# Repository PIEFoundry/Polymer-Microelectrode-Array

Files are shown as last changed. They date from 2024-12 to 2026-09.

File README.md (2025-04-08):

# Polymer Microelectrode Array
This repository contains all files relevant to the design and manufacture of the PIE Foundry polymer microelectrode arrays. For more information about the PIE Foundry, visit our [website](https://piefoundry.usc.edu/). <br>
Please cite this repository using the DOI below <br> 

## Organization
[Protocols](/Protocols) directory holds up-to-date protocols and subprotocols for PMEA microfabrication and PCB attachment/packaging. PDF files are updated with each release. <br>
[Designs](/Designs) directory holds lithographic designs of open-source PMEAs produced by the PIE Foundry, including component designs for lithographic masks, and PCB designs of common adapter boards. Lithographic designs are stored as .dxf and PCB designs are stored as gerber files and Eagle schematics. <Br>
[Resource](/Resources/) directory holds PIE Foundry generated Eagle libraries, including for common PMEA wirebond connector layouts and Omnetics brand analog connector solder pad layouts, as well as useful solid files. Solid files are stored in STEP format. 

## License
All files in this repository are released under the CC-BY 4.0 International copyright license

## Disclaimer
The contents of this repository are subject to revision. No representation or warranty, express or implied, is provided in relation to the accuracy, correctness, completeness, or reliability of the information, opinions, or conclusions expressed in this repository.

The contents of this repository (the “Materials”) are experimental in nature and should be used with prudence and appropriate caution. Any use is voluntary and at your own risk.

The Materials are made available “as is” by USC (the University of Southern California and its trustees, directors, officers, employees, faculty, students, agents, affiliated organizations and their insurance carriers, if any), and any other contributors to this repository (collectively, “Providers”). Providers expressly disclaim all warranties, express or implied, arising in connection with the Materials, or arising out of a course of performance, dealing, or trade usage, including, without limitation, any warranties of title, noninfringement, merchantability, or fitness for a particular purpose.

Any user of the Materials agrees to forever indemnify, defend, and hold harmless Providers from and against, and to waive any and all claims against Providers for any and all claims, suits, demands, liability, loss or damage whatsoever, including attorneys' fees, whether direct or consequential, on account of any loss, injury, death or damage to any person or (including without limitation all agents and employees of Providers and all property owned by, leased to or used by either Providers) or on account of any loss or damages to business or reputations or privacy of any persons, arising in whole or in part in any way from use of the Materials or in any way connected therewith or in any way related thereto.

The Materials, any related materials, and all intellectual property therein, are owned by Providers.

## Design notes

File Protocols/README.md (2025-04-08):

These are the current microfabrication, packaging, and assembly protocols for manufacturing Parylene C based microelectrode arrays. Protocols were developed by PIE Foundry staff and derived from work at the [Biomedical Microsystems Laboratory](http://biomems.usc.edu/) of Dr. Ellis Meng at the University of Southern California. 

Contributors: Kee Scholten, Jessica Ortigoza-Diaz, James Yoo, Artin Petrossians, Rachael Gallonio, Steven Baldwin, Ellis Meng

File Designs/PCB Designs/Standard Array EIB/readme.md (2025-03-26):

PCB design file set for 64 channel Standard Array EIB

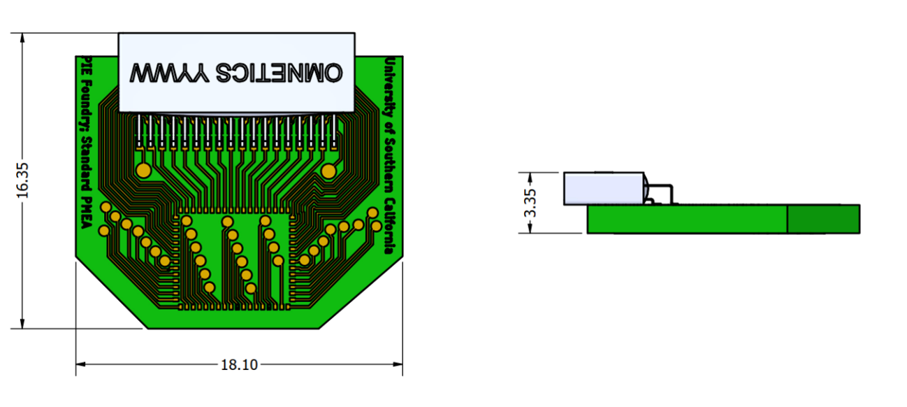
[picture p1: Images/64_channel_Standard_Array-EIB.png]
Image of a printed circuit board schematic


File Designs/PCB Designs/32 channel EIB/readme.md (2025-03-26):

PCB design file set for 32 channel EIB 

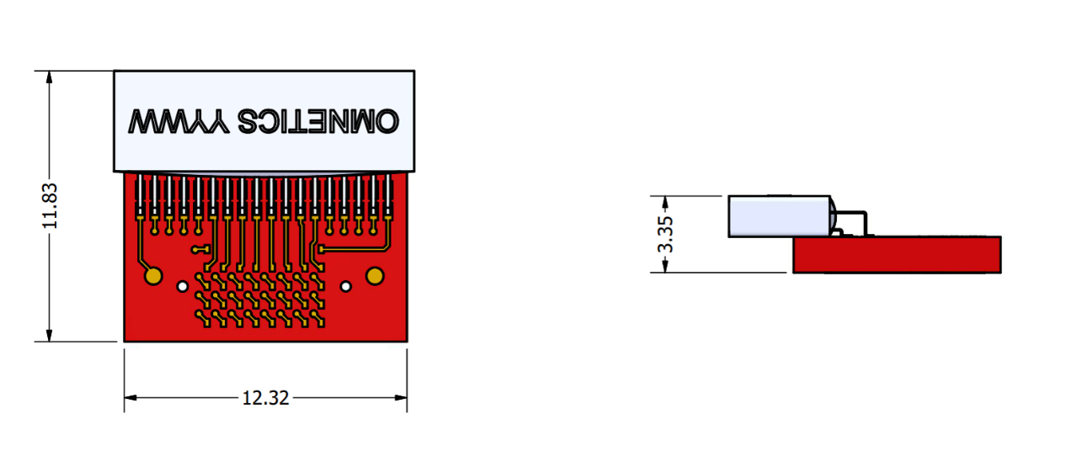
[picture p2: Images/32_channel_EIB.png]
Image of a printed circuit board schematic


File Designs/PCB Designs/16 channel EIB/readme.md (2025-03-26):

PCB design file set for 16 channel EIB 

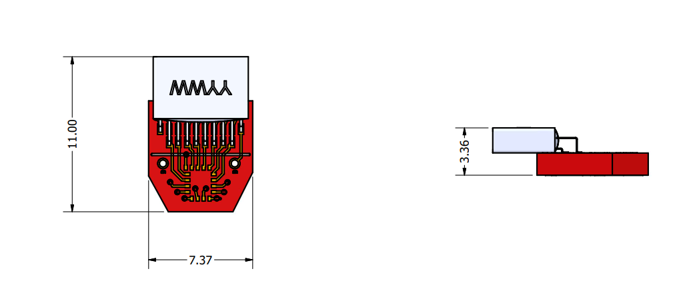
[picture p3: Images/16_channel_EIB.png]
Image of a printed circuit board schematic


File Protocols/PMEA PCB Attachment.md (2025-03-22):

# Protocol: Packaging and Assembly of Parylene Microelectrode Arrays

Description: This document details the packaging and assembly protocol for connectorization of Parylene C microelectrode arrays (MEAs) with printed circuit board (PCB) connectors.

_Note: Standard equipment and materials (e.g. tweezers, microscopes, DI water, cleanroom wipes, N<sub>2</sub> gun, scale, etc.) are not listed in materials lists._

Table of Contents

1. [Printed Circuit Board (PCB) Preparation](#1-pcb-preparation)
   * [Separate, Sand, and Clean](#11-separate-sand-and-clean)
   * [Bump Contact Pads](#12-bump-contact-pads)
   * [Coin Contact Pads](#13-coin-contact-pads)
2. [Component/Connector Soldering](#2-componentconnector-soldering)
      * [Apply Solder Paste](#21-apply-solder-paste)
      * [Align and Attach Components](#22-align-and-attach-components)
      * [Reflow Solder](#23-reflow-solder)
      * [Clean PCB](#24-clean-pcb)
3. [Parylene C Coating](#3-parylene-c-coating)
      * [Mask Components](#31-mask-components)
      * [Deposit Parylene C](#32-deposit-parylene-c)
4. [Component Potting & Ground Attachment](#4-component-potting--ground-attachment)
      * [Pot Connectors](#41-pot-connectors)
      * [Demask](#42-demask)
      * [Solder Ground Wires](#43-solder-ground-wires)
5. [Polymer Ultrasonic on Bump (PUB) Bonding](#5-polymer-ultrasonic-on-bump-pub-bonding)
      * [Align MEA to PCB](#51-align-mea-to-pcb)
      * [PUB Bond MEA to PCB](#52-pub-bond-mea-to-pcb)
6. [Underfill & Overcoat](#6-underfill--overcoat)
      * [Underfill](#61-underfill)
      * [Overcoat](#62-overcoat)
<ol type="A">
  <li>     <a href="#a-material-sources">Material Source</a>   </li>
  <li>     <a href="#b-equipment-models">Equipment Models</a>   </li>
</ol>

## 1. PCB Preparation

### 1.1 Separate, Sand, and Clean
_Note: This section only applies to FR-4 PCBs_

Materials: 
* *400 grit sandpaper (or similar)*
* *Isopropanol*

Equipment: 
* *Ultrasonic cleaner*

Process:
1. Separate PCBs from panel.
2. Sand edges with 400 grit sandpaper.
   1. With sandpaper flat on desk or table, run PCB edges across sandpaper until smooth. Apply even force to keep edges flat.
3. Clean PCBs in ultrasonic cleaner.
   1. Isopropanol for 10 minutes
   2. DI water for 10 minutes
4. Blow dry with N<sub>2</sub>

### 1.2 Bump Contact Pads

Equipment: 
* *Ultrasonic wire bonder (ball type)*

Process:
1. Using a ball-bonder in bump mode, place two gold bumps, approximately 75 microns in diameter, on the center of each contact pad on the PCB.
    1. Bump parameters
   <br>Tool: Hybond Model 626
   <br>Gold wire: 1 mil
   <br>Capillary attachment: Small Precision Tools UTSDIC-38HH-AZM-1/16-19MM
   <br>Stage Temperature: 140 °C
   <br>Ultrasonic Power: 180 mW
   <br>Time: 180 miliseconds
   <br>Force: 12 grams
   <br>EFO Power: 29 arbitrary units
   <br>Pull Length: 02 units
   <br>Tail Length: 27 units
    <br>Loop Height: 010 units

2. For best results ensure PCB is flush with stage and held tightly by clamps and/or vacuum chuck. For flex-PCBs additional fixturing may be required. Above parameters are tailored for FR-4 and may need to be modified for flex-PCB.

### 1.3 Coin Contact Pads

Equipment: 
* *Ultrasonic wire bonder (ball or wedge type)*

Process:
1. Using an ultrasonic ball bonder or wedge bonder with a tape-automated-bonding (TAB) tool attachment flatten and level each gold bump into a ‘coin’. Each bump will be hit twice with the two separate settings below.
    1. Tool: Hybond Model 572a
   <br>Tab attachment: Small Precision Tools 7045W-C-9060-3/4-M
   <br>Stage Temperature: Room temperature  
   <br>Step #1:  
   <br>Ultrasonic Power: 3 units
   <br>Time: 4.4 units
   <br>Force: 5.0 units  
   <br>Step #2:  
   <br>Ultrasonic Power: 3.4 units
   <br>Time: 4.4 units
   <br>Force: 7.0 units

2. Resulting coins should be approximately 30 microns tall and 100 microns in diameter.

## 2. Component/Connector Soldering

### 2.1 Apply Solder Paste

Materials: 
* *Lead-free solder paste*
* *23-gauge Luer stub (4 mm in length)*

Equipment: 
* *Pneumatic fluid dispenser*
* *Stereoscope*

Process:
1. Remove solder-paste from refrigerator and allow to reach room temperature, approximately 20 minutes.
2. Connect solder-paste cartridge to fluid dispenser.
    1. Attach Luer stub
    2. Set dispenser to 15 PSI
3. With aid of stereoscope, apply a small dot of solder past to each solder pad. Paste should be dispensed in one motion for each pad.

### 2.2 Align and Attach Components

Equipment: 
* *Soldering iron*
* *Stereoscope*

Process:
1. With aid of stereoscope carefully place and align components onto solder pads.
    1. For components such as Omnetics connectors which often hang off the edge of the PCB, a spacer may be necessary.
2. With the soldering iron set to~650 °F solder a single outside leg of each component.
    1. If necessary, adjust alignment and solder a leg on the other side of the component.

### 2.3 Reflow Solder

Materials: 
* *Ceramic plate or stainless-steel tray*

Equipment:
* *Reflow oven*

Process:
1. Place PCBs to be soldered in stainless-steel tray or onto ceramic plate and place on reflow oven platform.
2. Solder components to PCB using reflow oven with following profile:
    1. Tool: DDM Novastar Model GF-B
   <br>Temperature: 240 °C
   <br>Time<sub>a</sub>: 90 seconds
   <br>Time<sub>b</sub>: 300 seconds

### 2.4 Clean PCB

Materials: 
* *Lead-free flux remover*
* *Isopropanol*

Equipment: 
* *Ultrasonic cleaner*

Process:
1. Descum (clean) wafers in the RIE, two 4” wafers at the same time, using the following recipe:  
    150 mT, 100 W, 50 sccm O<sub>2</sub>, 180 s.

## 3. Parylene C Coating

### 3.1 Mask Components

Materials:
* *PTFE tape*

Process:
1. Using thin PTFE tape, cover the bond pads, faces of all connectors, solder connectors for ground/reference wire attachment, and any other surface needed to be deinsulated
    1. PCB designs with vias may need to be masked on both sides to prevent Parylene C from diffusing through vias underneath masking tape.
    2. Tape must be snug; use tweezer, dental pick, or other small metal tool to firmly laminate tape over all surfaces.

### 3.2 Deposit Parylene C

Materials:
* *Parylene C dimer*

Equipment:
* *Parylene PVD*

Process:
1. Deposit 10 µm of Parylene C onto the PCBs. See Parylene C Deposition Protocol.
    1. 30 g of dimer is typical but will depend on number and size of PCBs.
    2. As Parylene C layer on PCBs cannot be measured directly, reference slides should be included in coating.
    3. PCBs should be placed on sheet of aluminum foil in coating system to prevent them from sticking to shelves.

## 4. Component Potting & Ground Attachment

### 4.1 Pot Connectors

Materials: 
* *Medical grade epoxy*
* *23-gauge Luer stub*
* *3 cc dispenser barrel*
* *Dispenser cap*

Equipment: 
* *Pneumatic fluid-dispenser*
* *Bell jar*
* *Scale*
* *Oven*

Process:
1. Weigh out and thoroughly mix components of medical grade epoxy.
    1. For Epotek MED-302-3M (preferred) the ratio is 10:4.5.
    2. 1-2 g is sufficient
2. Decant epoxy into dispenser barrel and degas in bell jar under vacuum for 1 hour
    1. Barrel should be capped and stood vertically to prevent epoxy from spilling or leaking
3. Connect barrel to fluid dispenser.
    1. Attach Luer stub
    2. Set dispenser to 15 PSI
4. Apply a thick layer of epoxy to all exposed component legs.
5. Cure in oven according to epoxy curing schedule
    1. For MED-302-3M this is 2 hours at 80 °C

### 4.2 Demask

Materials:
* *Isopropanol*
* *Razor or X-Acto knife*

Equipment: 
* *Ultrasonic bath*
* *Stereoscope*

Process:
1. Using a fresh razor blade or X-Acto knife remove the Parylene C insulation from the masking tape.
2. Soak the masking tape with isopropanol and gently remove the tape from contact pads and solder connections.
3. Clean PCBs in ultrasonic cleaner.
    1. Isopropanol for 5 minutes
    2. DI water for 5 minutes
    3. Blow dry with N<sub>2</sub>

### 4.3 Solder Ground Wires

Materials:
* *Fine, insulated, stainless-steel wires (0.003” bare, 0.0055” coated, annealed)*
* *Lead-free solder*
* *Stainless steel flux*
* *Micro swab*
  
Equipment: 
* *Soldering iron*
* *Stereoscope*
* *Micro scissors*

Process:
1. Cut 8-10 cm lengths of stainless-steel wire (typically 2 per PCB) and remove 1 cm of insulation from proximal end, and 3 cm from the distal end.
    1. Use stainless steel micro scissors to carefully strip insulation.
    2. Length and number of ground wire may vary with project design
2. Thread proximal end of wire through appropriate plated-through-hole on PCB. Bend de-insulated end to prevent wire from pulling out.
3. Using micro swab, apply small dab of stainless-steel flux to soldering site.
4. With soldering iron set to 650 °F, solder wire to board using lead-free solder.
5. Trim excess wire from underside of PCB.
6. Repeat as needed for each wire.

## 5. Polymer Ultrasonic on Bump (PUB) Bonding

### 5.1 Align MEA to PCB

Materials:
* *Adhesive tape*
  
Equipment: 
* *Stereoscope*

Process:
1. Place MEA face down over PCB contact pads.
2. Using stereoscope, align MEA to contact pads and secure in place with small pieces of tape.
    1. It is very important that the Parylene C MEA lies as flat as possible. If necessary small drops of isopropanol can be used to pull the MEA taught to the PCB using surface tension.

### 5.2 PUB Bond MEA to PCB

Equipment:
* *Ultrasonic wire bonder (ball or wedge type)*

Process:
1. Using an ultrasonic wire bonder with a tape-automated bonding (TAB) tool attachment, weld each contact pad on the Parylene MEA to the corresponding PCB pad, using the flattened gold coins as an intermediary. Each pad will be hit twice with the two separate settings below.
    1. Tool: Hybond Model 572A
   <br> Tab attachment: Small Precision Tools 7045W-TI-10050-3/4-M
   <br> Stage Temperature: Room temperature
   <br> Step #1:
   <br> Ultrasonic Power: 8.0 units
   <br> Time: 3.0 units
   <br> Force: 6.5 units
   <br>Step #2:
   <br> Ultrasonic Power: 9.0 units
   <br> Time: 4.5 units
   <br> Force: 6.0 units

    2.  Take all measures to try and keep the MEA laminated to the PCB

## 6 Underfill & Overcoat

### 6.1 Underfill

Materials: 
* *Medical grade epoxy (thin)*
* *32-gauge Luer stub*
* *3 cc dispenser barrel*

Equipment: 
* *Pneumatic fluid-dispenser*
* *Scale*
* *Stereoscope*
* *Oven*

Process:
1. Weigh out and thoroughly mix components of medical grade epoxy.
    1. For Epotek MED-301 (preferred) the ratio is 20:5
    2. 1 g is sufficient
2. Fill cartridge with epoxy and connect barrel to fluid dispenser.
    1. Attach Luer stub
    2. Set dispenser to 10 PSI
3. Apply small drops of epoxy to the edges/corners of the MEA and allow to underfill the space between the MEA and the PCB.
4. Allow to cure at room temperature (overnight) or in oven at 65 °C for 1 hour.

### 6.2 Overcoat

Materials: 
* *Medical grade epoxy*
* *23-gauge Luer stub*
* *3 cc dispenser barrel*
* *Dispenser cap*

Equipment: 
* *Pneumatic fluid-dispenser*
* *Bell jar*
* *Scale*
* *Oven*

Process:
1. Weigh out and thoroughly mix components of medical grade epoxy.
    1. For Epotek MED-302-3M (preferred) the ratio is 10:4.5
    2. 1-2 g is sufficient
2. Decant epoxy into dispenser barrel and degas in bell jar under vacuum for 1 hour
    1. Barrel should be capped and stood vertically to prevent epoxy from spilling or leaking
3. Connect barrel to fluid dispenser.
    1. Attach Luer stub
    2. Set dispenser to 15 PSI
4. Apply a thick layer of epoxy to entire surface of PCB
5. Cure in oven according to epoxy curing schedule
    1. For MED-302-3M this is 2 hours at 80 °C
6. Repeat on opposite side
7. Material Sources

_Note: Standard materials (e.g. isopropanol, DI water, cleanroom wipes, etc.) are not listed_

## A. Material Sources
| **Material** | **Model #** | **Supplier** |
| --- | --- | --- |
| Parylene C dimer |     | Specialty Coating Systems, Indianapolis, IN |
| Lead-free solder paste | 4900 P SAC305 | MG Chemicals, Burlington, Ontario, Canada |
| Lead-free flux remover | ES1697 | Chemtronics, Kennesaw, Georgia |
| Medical grade epoxy (thick) | MED-302-3M | Epoxy Technology, Billerica, MA |
| Medical grade epoxy (thin) | MED-301 | Epoxy Technology, Billerica, MA |
| Stainless-steel flux |     | Superior Flux & Mfg. Co., Cleveland, OH |
| Stainless-steel wire | 790900 | A-M Systems Inc., Sequim, WA |
| Dispenser barrel |     | North Richland Hills, TX |

## B. Equipment Models

_Note: Standard equipment (e.g. tweezers, microscopes, N<sub>2</sub> gun, scale, etc.) are not listed_

| **Equipment** | **Model #** | **Supplier** |
| --- | --- | --- |
| Ultrasonic wire bonder (ball type) | 626 | Hybond Inc., Escondido, CA |
| Ultrasonic wire bonder (wedge type) | 572A | Hybond Inc., Escondido, CA |
| Ball-bonder capillary | UTSDIC-38HH-AZM-1/16-19MM | Small Precision Tools, Petaluma, CA |
| TAB tool | 7045W-C-9060-3/4-M | Small Precision Tools, Petaluma, CA |
| 7045W-TI-10050-3/4-M |
| Pneumatic fluid-dispenser | Performus III | Nordson, Westlake, OH |
| Reflow oven | GF-B | DDM Novastar, Ivyland, PA |
| Parylene PVD | PDS 2010 Labcoter | Specialty Coating Systems, Indianapolis, IN |

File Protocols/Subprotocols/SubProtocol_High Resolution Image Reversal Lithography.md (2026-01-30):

# Sub-Protocol: High Resolution Image Reversal Lithography

Description: This document details the protocol for the high-resolution image reversal lithography used to produce the lift-off profile for metal patterning in the PIE Foundry standard microfabrication process. It is tailored for use on Parylene C coated silicon wafers.

## Materials:

* *AZ5214-E Photoresist*
* *AZ340 Developer*
* *5 mL Polypropylene Syringe (per wafer)*
* *22-Gauge Luer Stub (per wafer)*

## Equipment:

* *OAI Model 200 Contact Mask Aligner and UV Source*
* *Electronic Micro Systems 1000-1 Hot plate*
* *YES CV200RFS Plasma Asher*
* *Laurell Technologies Photoresist Spinner Model WS-400B-6NPP Lite*
* *Vacuum oven with N<sub>2</sub>*
* *UV intensity meter*
* *IR temperature sensor*
* *Wafer centering tool*
* *HDPE trays for developer and water baths*
* *Wafer dipper/holding tool*

## Parameters:

### Spinner Recipe Program P  
1st Spin Speed: 500 RPM  
1st Spin Time: 10 seconds<br>
1st Spin Acceleration: acceleration level 8 (1088 RPM)  
<br>
2nd Spin Speed: 4200 RPM  
2nd Spin Time: 40 seconds<br>
2nd Spin Acceleration: acceleration level 8 (1088 RPM)

### Soft-Bake
Temperature: 110 °C
Time: 60 seconds

### 1st Exposure
Dose: 42 mJ/cm<sup>2</sup>
Time: 3.4 seconds
Intensity: 12.5 mW/cm<sup>2</sup>

### Image-Reversal Bake
Temperature: 110 °C
Time: 63 seconds

### 2nd Exposure
Dose: 280 mJ/cm<sup>2</sup><br>
Time: 22.4 seconds<br>
Intensity: 12.5 mW/cm<sup>2</sup>

### Develop
Concentration: 1:4 AZ340 developer to deionized water (200 mL total volume)<br>
Time: 18 seconds

## Process:

1.  Descum
    1. Descum (clean/roughen) wafers in the asher using the following recipe<br>
   300 mT, 100 W, 115 sccm O<sub>2</sub>, 300 seconds

2. Prepare Developer and Water Baths<br>
_Note: perform in chemical fume hood_
    1. Prepare a shallow HDPE tray full of DI water, and with a 1:4 mixture of AZ340 developer and DI water (200 mL total volume)
    <br> a. 200 mL of developer solution should be sufficient for 2 wafers

3. Dry-Bake<br>
_Note: this step should be performed immediately before photoresist deposition_
    1. Bake wafers at 60 °C in an oven under light vacuum (35-40 cmHg) and N<sub>2</sub> flow (15-20 sccm) for >15 minutes

4. Spin Photoresist<br>
_Note: Before coating wafers run 3 “dummy spins” using spare wafers to ensure spinner chamber environment is saturated with solvent from photoresist. This will prevent differences in resist thickness between first and last wafers in a run._
    1. Line sidewalls of spinner with aluminum foil to reduce mess
    2. Center wafer on spinner vacuum chuck using spinner centering tool and engage chuck vacuum
    <br> a. Spinner requires supply of clean dry air for vacuum to engage
    3. Deposit 3 mL of AZ5214-E photoresist from preprepared syringe onto center of wafer through 22-gauge Luer stub
    <br> a. Ensure there are no air bubbles in resist
    4. Close lid and run program
    <br> a. Spin on 500 RPM for 10 seconds
    <br> b. Spin 4200 RPM for 40 seconds

5. Soft-Bake
    1.Bake the wafer on hotplate for 1 minute at 110 °C. Calibrate temperature to IR gun and do not rely on hotplate reading
    2. Wafer should be placed in the center of the hot plate with flat facing forward. Use heat shield around hot plate
    3. After baking, store the wafer in black wafer storage box for at least 3 minutes

6. Vacuum Contact and Exposure
    1. Set the UV lamp to desired intensity and duration. Targeted dose is 42 mJ/cm<sup>2</sup>. Typical intensity is 12.5 mW/cm<sup>2</sup> for 3.4 seconds but can be adjusted depending on current lamp intensity
    2. Clean mask aligner vacuum chuck and mask holder of any particles. Place vacuum O-ring around vacuum chuck
    3. Place photomask feature (chrome) side down (facing vacuum chuck). Secure with mask holder vacuum and screw clamps
    4. Place wafer face up and centered on vacuum chuck. Turn on substrate vacuum
    5. Blow mask surface and wafer surface clean of particles with N<sub>2</sub> gun
    6. Engage N<sub>2</sub> purge
    7. Lower mask holder
    8. Raise wafer using Z-axis knob until mask appears flush with mask. Lower mask slightly and then use fine x/y/θ controls to center wafer under mask. Re-raise wafer
    9. Turn off substrate vacuum and engage contact vacuum. Open contact vacuum knob until vacuum gauge reads ~5” Hg. You may need to lower N<sub>2</sub> purge to create good seal. Please note, sufficient vacuum is only needed to create good contact between mask and wafer as indicated by appearance of Newton ring diffraction. Use the lowest possible vacuum setting that will achieve this effect
    10. Expose the wafer by carefully sliding the aligner assembly under the UV lamp. Wait for exposure, then carefully slide the assembly back to starting position
    11. Lower the contact vacuum level by turning the knob clockwise. Once closed, turn off the contact vacuum. If the N<sub>2</sub> purge level was decreased, return it to starting level. Re-engage the substrate vacuum and then gently lower the wafer. If the wafer does not move freely, pause, and wait before trying again
    12. Lower the wafer completely clear of the mask. Raise the mask holder. Dis-engage substrate vacuum and N<sub>2</sub> purge. Remove wafer

7. Image-Reversal-Bake
    1. Bake the wafer on hotplate for 63 seconds at 110 °C ± 0.5 °C. Calibrate temperature to IR gun and do not rely on hotplate reading
    <br> a. This step is critical. Avoid any variation in time or temperature
    2. Wafer should be placed in the center of the hot plate with flat facing forward. Use heat shield around hot plate
    3. After baking, store the wafer in black wafer storage box for at least 3 minutes

8. Flood Exposure
    1. Set the UV lamp to desired intensity and duration. Targeted dose is 280 mJ/cm<sup>2</sup>. Typical intensity is 12.5 mW/cm<sup>2</sup> for 22.4 seconds but can be adjusted depending on current lamp intensity
    2. Remove mask from mask holder and store
    3. Place wafer face up and centered on vacuum chuck. Turn on substrate vacuum
    4. Blow wafer surface clean of particles with N<sub>2</sub> gun
    5. Expose the wafer by carefully sliding the aligner assembly under the UV lamp. Wait for exposure, then carefully slide the assembly back to starting position
    6. Dis-engage substrate vacuum. Remove wafer

9. Quench in Deionized Water
    1. Immediately place wafer in shallow bath of DI water and let soak for 3 minutes to avoid heating and reduce gas bubble formation

10. Develop
    1. Develop wafer in 1:4 solution of AZ340 to DI water for 18 seconds with mild agitation
    2. Immediately rinse in DI water bath and rinse 3× in water
    3. Blow dry with N<sub>2</sub>

11. Inspect
    1. Inspect under compound microscope with yellow light filter

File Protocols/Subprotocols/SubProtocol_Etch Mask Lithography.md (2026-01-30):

# Sub-Protocol: Etch Mask Lithography

Description: This document details the protocol for the photolithography used to produce the etch mask used to define the pattern in (deep) reactive ion etching steps in the PIE Foundry MEA microfabrication process. This protocol is tailored for use on Parylene C coated silicon wafers.

## Materials:

* *AZ 12XT-20PL-15 Photoresist*
* *726 MIF Developer*
* *5 mL Polypropylene Syringe (per wafer)*

## Equipment:

* *OAI Model 200 Contact Mask Aligner and UV Source*
* *Electronic Micro Systems 1000-1 Hot plate*
* *YES CV200RFS Plasma Asher*
* *Laurell Technologies Photoresist Spinner Model WS-400B-6NPP Lite*
* *Vacuum oven with N<sub>2</sub>*
* *UV intensity meter*
* *IR temperature sensor*
* *Wafer centering tool*
* *HDPE trays for developer and water baths*
* *Wafer dipper/holding tool*

## Parameters

Spinner Recipe Program T  
1st Spin Speed: 500 RPM  
1st Spin Time: 10 seconds

1st Spin Acceleration: acceleration level 2 (low acceleration/deceleration)  
2nd Spin Speed: 2000 RPM  
2nd Spin Time: 45 seconds

2nd Spin Acceleration: acceleration level 2 (low acceleration/deceleration)

### Soft-Bake:<br>
Temperature: 110 °C<br>Time: 180 seconds 

### Exposure<br>
Dose: 117.5 mJ/cm<sup>2</sup><br>
Time: 9.4 seconds<br>
Intensity: 12.5 mW/cm<sup>2</sup>

### Post-Exposure Bake

Temperature: 90 °C<br>
Time: 90 seconds

### Develop

Concentration: 726 MIF developer as bottled<br>
Time: 75 seconds (approximate)

## Process:

1. Descum
    1. Descum (clean/roughen) wafers in the asher using the following recipe  :
    2. 300 mT, 100 W, 115 sccm O<sub>2</sub>, 300 seconds
2. Prepare Developer and Water Baths<br>_Note: perform in chemical fume hood_
    1. Prepare a shallow HDPE tray full of DI water, and another with 726 MIF developer
    <br> a. ~250 mL of 726 MIF developer should be sufficient for 6 wafers

3. Dry-Bake<br>_Note: this step should be performed immediately before photoresist deposition_
    1. Bake wafers at 60 °C in an oven under light vacuum (35-40 cmHg) and N¬2 flow (15-20 sccm) for >15 minutes

4. Spin Photoresist<br>_Note: Before coating wafers run 3 “dummy spins” using spare wafers to ensure spinner chamber environment is saturated with solvent from photoresist. This will prevent differences in resist thickness between first and last wafers in a run._
    1. Line sidewalls of spinner with aluminum foil to reduce mess
    2. Center wafer on spinner vacuum chuck using spinner centering tool and engage chuck vacuum
    <br> a. Spinner requires supply of clean dry air for vacuum to engage
    3. Deposit 3 mL of AZ 12XT-20PL-15 photoresist from preprepared syringe onto center of wafer
    <br> a. Ensure there are no air bubbles in resist
    4. Close lid and run program
    <br> a. Spin on 500 RPM for 10 seconds
    <br> b. Spin 2000 RPM for 45 seconds <br>_Note: Low acceleration/deceleration helps prevent spin defects_

5. Edge Bead Removal
    1. Remove photoresist edge bead to improve lithographic alignment. [See Edge Bead Removal Subprotocol](SubProtocol_Edge%20Bead%20Removal.md) 

6. Soft-Bake
    1. Bake the wafer on hotplate for 3 minutes at 110 °C. Calibrate temperature to IR gun and do not rely on hotplate reading
    2. Wafer should be placed in the center of the hot plate with flat facing forward. Use heat shield around hot plate
    3. After baking, store the wafer in black wafer storage box for at least 3 minutes

7. Align, Contact, and Exposure
    1. Set the UV lamp to desired intensity and duration. Targeted dose is 117.5 mJ/cm<sup>2</sup>. Typical intensity is 12.5 mW/cm<sup>2</sup> for 14.8 seconds but can be adjusted depending on current lamp intensity
    2. Clean mask aligner vacuum chuck and mask holder of any particles. Remove vacuum O-ring around vacuum chuck if present
    3. Place photomask feature (chrome) side down (facing vacuum chuck). Secure with mask holder vacuum and screw clamps
    4. Place wafer face up and centered on vacuum chuck. Turn on substrate vacuum
    5. Blow mask surface and wafer surface clean of particles with N<sub>2</sub> gun
    6. Engage N<sub>2</sub> purge
    7. Lower mask holder
    8. Raise wafer using Z-axis knob until mask is flush with mask. Engage ball lock
    9. Reduce Z-axis control sensitivity. While looking through aligner microscope on lowest magnification, lower wafer until it just barely disengages with mask. Confirm that wafer is now able to move freely using fine X/Y/θ controls
    10. Moving back and forth between left and right alignment marks, align the angle (theta) of the mask and wafer
    11. Once wafer and mask are aligned in theta, ensure X and Y coordinates are aligned
    12. Increase magnification to higher objective lens then repeat 5.10-5.12
    13. Once satisfied, raise the wafer to contact, confirm alignment has not drifted. Disengage N<sub>2</sub> purge
    14. Expose the wafer by carefully sliding the aligner assembly under the UV lamp. Wait for exposure, then carefully slide the assembly back to starting position
    15. Re-engage N<sub>2</sub> purge. Gently lower the wafer. If the wafer does not move freely, pause, and wait before trying again
    16. Once the wafer moves freely, return Z-axis sensitivity to starting level and lower the wafer completely clear of the mask. Raise the mask holder. Dis-engage substrate vacuum and N<sub>2</sub> purge. Remove wafer

8. Post-Exposure-Bake
    1. Bake the wafer on hotplate for 90 seconds at 90 °C. Calibrate temperature to IR gun and do not rely on hotplate reading
    2. Wafer should be placed in the center of the hot plate with flat facing forward. Use heat shield around hot plate
    3. Allow wafer to fully cool before development

9. Develop
    1. Develop wafer in shallow bath of 726 MIF developer for approximately 75 seconds
    <br> a. Development time is dependent on area of exposed features and will vary between mask-sets
    2. Immediately rinse in DI water bath and rinse 3× in water
    3. Blow dry with N<sub>2</sub>

10. Inspect
    1. Inspect under compound microscope with yellow light filter

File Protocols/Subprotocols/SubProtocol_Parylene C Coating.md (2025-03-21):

# Sub-Protocol: Parylene C Coating

Description: This document details the protocol for coating silicon wafers (or similar materials) in Parylene C using a room temperature vapor deposition method.

_Note: Items not allowed in chamber include wood or wood products, scotch tape, liquids, or any substance likely to off-gas while under vacuum._

## Materials:
* *2% Micro-90 Solution*
* *TexWipe Cloths*
* *Parylene C Dimer*  
* *Parafilm*
* *Aluminum Foil (Contaminant-Free/Vacuum Grade)*
* *Scotch-Brite Pads*

## Equipment:
* *Specialty Coating Systems PDS 2010 Labcoter 2 Parylene Deposition System*
* *FTS Systems Flexi-Cool Mechanical Chiller and Cold Trap Probe*
* *Rotating shelf*
* *Digital scale*
* *Boat form (metal tube)*

## Parameters:
Vaporizer heater: 175 °C<br>
Pressure set point: Base (as measured during tool calibration) + 15 vacuum units (typically 35)<br>
Pyrolysis heater: 690 °C

## Process:
1. Clean and Setup (0.5 hours)
   1. Consult log to estimate the amount of Parylene C dimer required for targeted coating thickness. Most current measurements as of 12/16/2024 suggest 32-34 grams for 10 microns across 12 4” silicon wafers. Dimer mass to thickness ratio is determined by loading of the chamber and will be different for tools using different shelving units
   2. Weigh out Parylene C dimer in cleanroom using the scale. Log mass to the tenth of a gram. Seal Parylene C dimer bottle with parafilm
   3. Fill out log-sheet. Every 5th run (i.e. runs numbered 5, 10, 15, etc.) consult maintenance schedule, document, and notify super-user
   4. Check cold-trap, vaporizer door, and chamber lid O-rings to make sure each is clean and will form a good seal. If necessary, clean chamber lid O-ring by using Kapton tape adhesive to remove residue. Replace any cracked or badly fouled O-rings and notify super-user to replace in inventory
   5. During normal setup and operation, do NOT remove chamber base L-gasket. The gasket should only be disturbed if the tool is unable to pump down to base vacuum and troubleshooting is required
   6. Wipe all interior surfaces of the machine (chamber lid, rotating table, bottom plate, baffle, etc.) and the cold trap probe with a TexWipe cloth wetted with Micro-90 solution. Do not wipe the shelf as this can trap fibers. Thoroughly dry all wiped surfaces
   7. Place the Flexi-Cool cold trap probe into the cold trap in the coating system
   8. Place the rotating shelf onto the base
   9. Place your wafers onto the shelves, flats facing inward. Each shelf can accommodate 2 4” wafers. Ensure no sample extends beyond the edge of the rotating table
   10. Carefully lower chamber around shelf and place chamber lid on top of chamber

2. Construct Dimer Boat
   1. Cut a rectangular piece of aluminum foil 11x4 inches in dimension and curl the foil around the outsider diameter of the boat form (metal tube). Face shiniest side of the foil toward boat form. Fold in the ends of the foil and remove boat from the form
   <br> a. The dimer boat must be no more than 7.5 inches long.
   2. Pour the Parylene C dimer pellets into the foil boat and load the boat into the vaporizer
   <br> a. When loading the boat, place it only as far into the vaporizer tube as necessary and do not push the foil boat towards the back of the vaporizer tube.
   3. Close and lock the vaporizer door
   
3. Run Parylene C Coating System (min. 2 hours)
   1. Twist the “Emergency Stop” button until it pops
   2. Push “Main Power” button. Wait until all the controllers on the display panel to activate and display current measurement readings
   3. Turn the “Vacuum” knob to “Vacuum”. Initial vacuum reading should be around 1000 units. Press down on the lid for the first 20 seconds to help establish a good seal. The vacuum gauge should reach ~100 units in approximately 2 minutes. If not, there may be a leak, or an off-gassing sample
   4. Once the vacuum gauge reads below 100 units turn on the chiller. Wait a minimum of 45 minutes from this point before starting the deposition process
   5. Wait until the vacuum level has reached 5 units (or lower) AND 45 minutes have elapsed since turning on the chiller. Turn the “Furnace” and “Vaporizer” knobs to “Enable”, and then press the “Process Start/Stop” button. The green button should now be illuminated
   6.  Wait for deposition<br>
    For coating to begin, all the following must occur:
    <br> a. The chamber gauge must reach 135 °C.
        <br> b. The furnace must reach 690 °C.
        <br> c.  The vacuum reading must be less than 11.
   7. If any of these conditions are not met, something is wrong. Abort the run and contact super-user
   8. The machine will run for several hours depending on the coating thickness. The run will stop automatically, and the tool will begin to cool down when the process is complete. This will be indicated by a blinking green light on the “Process Start/Stop” button

4. Cool Down and Cleanup (~1 hour)
   1. Wait until the vaporizer temperature is below 90 °C
   2.  Turn off the chiller and wait > 5 minutes
   3.  Press the “Process Start/Stop” button
   4.  Turn the “Furnace” and “Vaporizer” knobs to “Disable”
   5.  Turn the “Vacuum: knob to “Vent”. Wait until vacuum gauge reads ~1000 units
   6.  Push the “Emergency Stop” button to power off coating system
   7.  Carefully remove the cold trap probe from the system and place in the holder to warm
   8.  Remove chamber lid
   9.  Remove and store samples
   10.  Peel Parylene C from the inside surfaces: chamber, chamber lid, rotating table, bottom plate, watch glass. If the Parylene C film is very thin (<3 microns) leave until the following run
   11.   Open vaporizer and discard the used foil boat. Remove any Parylene C residue from the outside of the vaporizer tube using a plastic chisel. Clean the inside of the vaporizer tube using the tube brush. Vacuum out any residue
   12.  Wipe the inside surfaces of the chamber (but not the vaporizer or shelf) with a TexWipe cloth wetted with Micro-90 solution
   13.  Outside of the cleanroom scrub the cold trap probe completely clean using a green Scotch-Brite pad. Polish with a TexWipe cloth and Micro-90 solution. Any cloudiness or residue will lead to rust spots, which is good for neither the probe nor the pump. Return the chiller and cold trap to the cleanroom
   14.  Log any issues or observations in the logbook

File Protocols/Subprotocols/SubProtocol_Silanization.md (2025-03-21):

# Sub-Protocol: Silanization

Description: This document details the protocol for the establishing a monolayer of A-174 silane between the metal layer and Parylene C insulation to improve inter-layer adhesion.

## Materials:

* *A-174 Silane*
* *Isopropanol*
* *Aluminum foil*
  
## Equipment:

* *Glass dishes designated for A-174 silane*
* *Graduated cylinder designated for A-174 silane*
* *Crystalizing dish labeled for A-174*
* *Wafer cassette designated for A-174*
* *Stirring rod*

## Process:

1. Prepare Silane Mixture
   1. Prepare a mixture of 900 mL DI water, 900 mL isopropanol, and 9 mL A-174 silane in a large glass beaker (volume ratio of A-174:IPA:DI water is 1:100:100)
   <br> a. This volume is used for batches of 12 wafers; smaller quantities using the same ratio can be used for smaller batches
   <br> b. Use designated graduated cylinders for the silane mix
   2. Gently stir the mixture for 30 seconds. Cover the beaker with aluminum foil and let sit for at least 2.5 hours, but no more than 24 hours.

2. Soak Wafers
   1. Transfer the A-174 mixture into crystallizing dish.
   2.  Soak wafers face up in wafer cassette in the A-174 mixture for 30 minutes. Wafers must be fully submerged.

3. Air Dry
   1. Remove the wafers and place on TexWipe in the fume hood face up and air dry for 30 minutes

4. Isopropanol Rinse
   1. Rinse the wafers thoroughly with IPA for 30-60 seconds using a squeeze bottle

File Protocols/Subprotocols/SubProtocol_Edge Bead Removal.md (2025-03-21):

# Sub-Protocol: Edge Bead Removal

Description: This document details the protocol for removing edge beads from wafers after spin-coating photoresist.

## Materials:

* *Edge Bead Removal Solvent*
* *Small magnet*
* *Microfiber swab*

## Equipment:

* *Laurell Technologies Photoresist Spinner Model WS-400B-6NPP Lite*
* *EBR Shield*
* *Wafer centering tool*

## Parameters

Recipe Program E  
1st Spin Speed: 200 RPM  
1st Spin Time: 5 seconds  
2nd Spin Speed: 750 RPM  
2nd Spin Time: 40 seconds

## Process:

1. Prepare spinner
    1. Place and center wafer on spinner using wafer centering tool. Typically this protocol is performed immediately following photoresist spinning and so this step is unnecessary
    2. Carefully lower EBR shield (black plastic cylinder) over wafer, without touching the wafer. With spinner lid still open, place magnet over lid sensor to override interlock. If necessary, use double sided tape to hold magnets in place

2. Prepare EBR solvent
    1. Fill a small glass beaker with EBR solvent and soak a large microfiber swab with solvent

3. Edge Bead Removal
    1. Turn the wafer such that the flat faces ‘3 o’clock’. Blot away excess solvent from the swab and place it on the edge of the wafer such that the swab is only just in contact with the edge bead. Start the program and use the first 5 seconds to reposition the swab if necessary. After 20 seconds, retract the swab and allow the wafer to spin dry

4. Repeat if necessary

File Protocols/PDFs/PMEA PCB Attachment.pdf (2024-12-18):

Polymer Implantable Electrode Foundry
Packaging and Assembly of Parylene Microelectrode Arrays | Date: 12/17/2024
Prepared by: PIE Foundry | Reviewed by: Kee Scholten | Page 1 of 8

## Protocol: Packaging and Assembly of Parylene Microelectrode Arrays

Description: This document details the packaging and assembly protocol for connectorization of Parylene C microelectrode arrays (MEAs) with printed circuit board (PCB) connectors.

Note: Standard equipment and materials (e.g. tweezers, microscopes, DI water, cleanroom wipes, N2 gun, scale, etc.) are not listed in materials lists.

## Table of Contents

Prepared by: PIE Foundry | Reviewed by: Kee Scholten | Page 2 of 8

### 1 PCB PREPARATION

### 1.1 SEPARATE, SAND, AND CLEAN

Materials: | 400 grit sandpaper (or similar)
| Isopropanol
Equipment: | Ultrasonic cleaner
Note: This section only applies to FR-4 PCBs
1. Separate PCBs from panel.
2. Sand edges with 400 grit sandpaper.
a. With sandpaper flat on desk or table, run PCB edges across sandpaper until smooth. Apply
| even force to keep edges flat.
3. Clean PCBs in ultrasonic cleaner.
a. Isopropanol for 10 minutes
b. DI water for 10 minutes

### 4. Blow dry with N2

1.2 ‘BUMP’ CONTACT PADS
Equipment: Ultrasonic wire bonder (ball type)

### 1. Using a ball-bonder in bump mode, place two gold bumps, approximately 75 microns in

diameter, on the center of each contact pad on the PCB.
a. Bump parameters
| Tool: Hybond Model 626
| Gold wire: 1 mil
| Capillary attachment: Small Precision Tools UTSDIC-38HH-AZM-1/16-19MM
| Stage Temperature: 140 °C
| Ultrasonic Power: 180 mW
| Time: 180 miliseconds
| Force: 12 grams
| EFO Power: 29 arbitrary units
| Pull Length: 02 units
| Tail Length: 27 units
| Loop Height: 010 units
2. For best results ensure PCB is flush with stage and held tightly by clamps and/or vacuum chuck. For flex-PCBs additional fixturing may be required. Above parameters are tailored for FR-4 and may need to be modified for flex-PCB.

1.3 ‘COIN’ CONTACT PADS
Equipment: Ultrasonic wire bonder (ball or wedge type)
1. Using an ultrasonic ball bonder or wedge bonder with a tape-automated-bonding (TAB) tool attachment flatten and level each gold bump into a ‘coin’. Each bump will be hit twice with the two separate settings below.
a. Tool: Hybond Model 572a

Prepared by: PIE Foundry | Reviewed by: Kee Scholten | Page 3 of 8

Tab attachment: Small Precision Tools 7045W-C-9060-3/4-M Stage Temperature: Room temperature
Step #1:
Ultrasonic Power: 3 units
Time: 4.4 units
Force: 5.0 units
Step #2:
Ultrasonic Power: 3.4 units Time: 4.4 units
Force: 7.0 units
2. Resulting coins should be approximately 30 microns tall and 100 microns in diameter.

### 2 COMPONENT/CONNECTOR SOLDERING

### 2.1 APPLY SOLDER PASTE

Materials: | Lead-free solder paste
| 23-gauge Luer stub (4 mm in length)
Equipment: | Pneumatic fluid dispenser
| Stereoscope
1. Remove solder-paste from refrigerator and allow to reach room temperature, approximately 20 minutes.
2. Connect solder-paste cartridge to fluid dispenser.
a. Attach Luer stub
b. Set dispenser to 15 PSI
3. With aid of stereoscope, apply a small dot of solder past to each solder pad. Paste should be dispensed in one motion for each pad.

### 2.2 ALIGN AND ATTACH COMPONENTS

Equipment: | Soldering iron
| Stereoscope
1. With aid of stereoscope carefully place and align components onto solder pads.
a. For components such as Omnetics connectors which often hang off the edge of the PCB,
| a spacer may be necessary.
2. With the soldering iron set to~650 °F solder a single outside leg of each component.
a. If necessary, adjust alignment and solder a leg on the other side of the component.

### 2.3 REFLOW SOLDER

Materials: | Ceramic plate or stainless-steel tray
Equipment: | Reflow oven
1. Place PCBs to be soldered in stainless-steel tray or onto ceramic plate and place on reflow oven platform.

Prepared by: PIE Foundry | Reviewed by: Kee Scholten | Page 4 of 8

### 2. Solder components to PCB using reflow oven with following profile:

a. Tool: DDM Novastar Model GF-B
Temperature: 240 °C
Timea: 90 seconds
Timeb: 300 seconds

### 2.4 CLEAN PCB

Materials: | Lead-free flux remover
| Isopropanol
Equipment: | Ultrasonic cleaner
1. Descum (clean) wafers in the RIE, two 4” wafers at the same time, using the following recipe: 150 mT, 100 W, 50 sccm O2, 180 s.

### 3 PARYLENE C COATING

### 3.1 MASK COMPONENTS

Materials: PTFE tape
1. Using thin PTFE tape, cover the bond pads, faces of all connectors, solder connectors for ground/reference wire attachment, and any other surface needed to be deinsulated
a. PCB designs with vias may need to be masked on both sides to prevent Parylene C from
| diffusing through vias underneath masking tape.
b. Tape must be snug; use tweezer, dental pick, or other small metal tool to firmly
| laminate tape over all surfaces.

### 3.2 DEPOSIT PARYLENE C

Materials: | Parylene C dimer
Equipment: | Parylene PVD
1. Deposit 10 µm of Parylene C onto the PCBs. See Parylene C Deposition Protocol.
a. 30 g of dimer is typical but will depend on number and size of PCBs.
b. As Parylene C layer on PCBs cannot be measured directly, reference slides should be
| included in coating.
c. PCBs should be placed on sheet of aluminum foil in coating system to prevent them
| from sticking to shelves.

### 4 COMPONENT POTTING & GROUND ATTACHMENT

### 4.1 POT CONNECTORS

Materials: | Medical grade epoxy
| 23-gauge Luer stub
| 3 cc dispenser barrel
| Dispenser cap

Prepared by: PIE Foundry | Reviewed by: Kee Scholten | Page 5 of 8
Equipment: | Pneumatic fluid-dispenser
| Bell jar
| Scale
| Oven
1. Weigh out and thoroughly mix components of medical grade epoxy.
a. For Epotek MED-302-3M (preferred) the ratio is 10:4.5.
b. 1-2 g is sufficient

### 2. Decant epoxy into dispenser barrel and degas in bell jar under vacuum for 1 hour

a. Barrel should be capped and stood vertically to prevent epoxy from spilling or leaking
3. Connect barrel to fluid dispenser.
a. Attach Luer stub
b. Set dispenser to 15 PSI
4. Apply a thick layer of epoxy to all exposed component legs.

### 5. Cure in oven according to epoxy curing schedule

a. For MED-302-3M this is 2 hours at 80 °C

### 4.2 DEMASK

Materials: | Isopropanol
| Razor or X-Acto knife
Equipment: | Ultrasonic cleaner
| Stereoscope
1. Using a fresh razor blade or X-Acto knife remove the Parylene C insulation from the masking tape.
2. Soak the masking tape with isopropanol and gently remove the tape from contact pads and solder connections.
3. Clean PCBs in ultrasonic cleaner.
c. Isopropanol for 5 minutes
d. DI water for 5 minutes

### 2. Blow dry with N2

### 4.3 SOLDER GROUND WIRES

Materials: | Fine, insulated, stainless-steel wires (0.003” bare, 0.0055” coated, annealed)
| Lead-free solder
| Stainless steel flux
| Micro swab
Equipment: | Soldering iron
| Stereoscope
| Micro scissors
1. Cut 8-10 cm lengths of stainless-steel wire (typically 2 per PCB) and remove 1 cm of insulation from proximal end, and 3 cm from the distal end.
a. Use stainless steel micro scissors to carefully strip insulation.
b. Length and number of ground wire may vary with project design

### 2. Thread proximal end of wire through appropriate plated-through-hole on PCB. Bend de-

insulated end to prevent wire from pulling out.

Prepared by: PIE Foundry | Reviewed by: Kee Scholten | Page 6 of 8
3. Using micro swab, apply small dab of stainless-steel flux to soldering site.
4. With soldering iron set to 650 °F, solder wire to board using lead-free solder.
5. Trim excess wire from underside of PCB.
6. Repeat as needed for each wire.

### 5 POLYMER ULTRASONIC ON BUMP (PUB) BONDING

### 5.1 ALIGN MEA TO PCB

Materials: | Adhesive tape
Equipment: | Stereoscope
1. Place MEA face down over PCB contact pads.
2. Using stereoscope, align MEA to contact pads and secure in place with small pieces of tape.
a. It is very important that the Parylene C MEA lies as flat as possible. If necessary small
| drops of isopropanol can be used to pull the MEA taught to the PCB using surface
| tension.

### 5.2 PUB BOND MEA TO PCB

Equipment: Ultrasonic wire bonder (ball or wedge type)
1. Using an ultrasonic wire bonder with a tape-automated bonding (TAB) tool attachment, weld each contact pad on the Parylene MEA to the corresponding PCB pad, using the flattened gold coins as an intermediary. Each pad will be hit twice with the two separate settings below.
a. Tool: Hybond Model 572A
| Tab attachment: Small Precision Tools 7045W-TI-10050-3/4-M
| Stage Temperature: Room temperature
| Step #1:
| Ultrasonic Power: 8.0 units
| Time: 3.0 units
| Force: 6.5 units
| Step #2:
| Ultrasonic Power: 9.0 units
| Time: 4.5 units
| Force: 6.0 units
b. Take all measures to try and keep the MEA laminated to the PCB

### 6 UNDERFILL & OVERCOAT

### 6.1 UNDERFILL

Materials: | Medical grade epoxy (thin)
| 32-gauge Luer stub

Prepared by: PIE Foundry | Reviewed by: Kee Scholten | Page 7 of 8

### 3 cc dispenser barrel

Equipment: | Pneumatic fluid-dispenser
| Scale
| Stereoscope
| Oven
1. Weigh out and thoroughly mix components of medical grade epoxy.
b. For Epotek MED-301 (preferred) the ratio is 20:5
c. 1 g is sufficient
2. Fill cartridge with epoxy and connect barrel to fluid dispenser.
a. Attach Luer stub
b. Set dispenser to 10 PSI
3. Apply small drops of epoxy to the edges/corners of the MEA and allow to underfill the space between the MEA and the PCB.
4. Allow to cure at room temperature (overnight) or in oven at 65 °C for 1 hour.

### 6.2 OVERCOAT

Materials: | Medical grade epoxy
| 23-gauge Luer stub
| 3 cc dispenser barrel
| Dispenser cap
Equipment: | Pneumatic fluid-dispenser
| Bell jar
| Scale
| Oven
1. Weigh out and thoroughly mix components of medical grade epoxy.
a. For Epotek MED-302-3M (preferred) the ratio is 10:4.5
b. 1-2 g is sufficient

### 2. Decant epoxy into dispenser barrel and degas in bell jar under vacuum for 1 hour

a. Barrel should be capped and stood vertically to prevent epoxy from spilling or leaking
3. Connect barrel to fluid dispenser.
a. Attach Luer stub
b. Set dispenser to 15 PSI

### 4. Apply a thick layer of epoxy to entire surface of PCB 5. Cure in oven according to epoxy curing schedule

a. For MED-302-3M this is 2 hours at 80 °C

### 6. Repeat on opposite side

Prepared by: PIE Foundry | Reviewed by: Kee Scholten | Page 8 of 8
A. MATERIAL SOURCES
Note: Standard materials (e.g. isopropanol, DI water, cleanroom wipes, etc.) are not listed
Material | Model # | Supplier
Parylene C dimer | | Specialty Coating Systems, Indianapolis, IN
Lead-free solder paste | 4900 P SAC305 | MG Chemicals, Burlington, Ontario, Canada
Lead-free flux remover | ES1697 | Chemtronics, Kennesaw, Georgia
Medical grade epoxy (thick) | MED-302-3M | Epoxy Technology, Billerica, MA
Medical grade epoxy (thin) | MED-301 | Epoxy Technology, Billerica, MA
Stainless-steel flux | | Superior Flux & Mfg. Co., Cleveland, OH
Stainless-steel wire | 790900 | A-M Systems Inc., Sequim, WA
Dispenser barrel | | North Richland Hills, TX
B. EQUIPMENT MODELS
Note: Standard equipment (e.g. tweezers, microscopes, N2 gun, scale, etc.) are not listed
Equipment | Model # | Supplier
Ultrasonic wire bonder (ball type) | 626 | Hybond Inc., Escondido, CA
Ultrasonic wire bonder (wedge type) | 572A | Hybond Inc., Escondido, CA
Ball-bonder capillary | UTSDIC-38HH-AZM-1/16-19MM | Small Precision Tools, Petaluma, CA
TAB tool | 7045W-C-9060-3/4-M | Small Precision Tools, Petaluma, CA 7045W-TI-10050-3/4-M
Pneumatic fluid-dispenser | Performus III | Nordson, Westlake, OH
Reflow oven | GF-B | DDM Novastar, Ivyland, PA
Parylene PVD | PDS 2010 Labcoter | Specialty Coating Systems, Indianapolis, IN

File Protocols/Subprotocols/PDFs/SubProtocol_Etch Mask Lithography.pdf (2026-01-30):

Polymer Implantable Electrode Foundry
Etch Mask Lithography v1.03 | Date: 01/30/2026
Prepared by: PIE Foundry | Reviewed by: Kee Scholten | Page 1 of 4

## Sub-Protocol: Etch Mask Lithography

Description: This document details the protocol for the photolithography used to produce the etch mask used to define the pattern in (deep) reactive ion etching steps in the PIE Foundry MEA microfabrication process. This protocol is tailored for use on Parylene C coated silicon wafers.

## MATERIALS

AZ 12XT-20PL-15Photoresist
726 MIF Developer
5 mL Polypropylene Syringe (per wafer)

## EQUIPMENT

OAI Model 200 Contact Mask Aligner and UV Source
Electronic Micro Systems 1000-1 Hot plate
YES CV200RFS Plasma Asher
Laurell Technologies Photoresist Spinner Model WS-400B-6NPP Lite Vacuum oven with N2
UV intensity meter
IR temperature sensor
Wafer centering tool
HDPE trays for developer and water baths Wafer dipper/holding tool

## PARAMETERS

Spinner Recipe Program T
1st Spin Speed: 500 RPM
1st Spin Time: 10 seconds
1st Spin Acceleration: acceleration level 2 2nd Spin Speed: 2000 RPM
2nd Spin Time: 45 seconds
2nd Spin Acceleration: acceleration level 2

Soft-Bake
Temperature: 110 °C
Time: 180 seconds

Exposure
Dose: 117.5 mJ/cm²
Time: 9.4 seconds
Intensity: 12.5 mW/cm²

Prepared by: PIE Foundry | Reviewed by: Kee Scholten | Page 2 of 4

Post-Exposure Bake
Temperature: 90 °C
Time: 90 seconds

Develop
Concentration: 726 MIF developer as bottled Time: 75 seconds (approximate)

## PROCESS

1. DESCUM
1.1. Descum (clean/roughen) wafers in the asher using the following recipe: 300 mT, 100 W, 300 seconds
2. PREPARE DEVELOPER AND WATER BATHS
Note: perform in chemical fume hood
2.1. Prepare a shallow HDPE tray full of DI water, and another with 726 MIF developer.
a. ~250 mL of 726 MIF developer should be sufficient for 6 wafers.

### 3. DRY-BAKE

Note: this step should be performed immediately before photoresist deposition
3.1. Bake wafers at 60 °C in an oven under light vacuum (35-40 cmHg) and N¬2 flow (15-20 sccm) for >15 minutes
4. SPIN PHOTORESIST
Note: Before coating wafers run 3 “dummy spins” using spare wafers to ensure spinner chamber environment is saturated with solvent from photoresist. This will prevent differences in resist thickness between first and last wafers in a run.
4.1. Line sidewalls of spinner with aluminum foil to reduce mess.
4.2. Center wafer on spinner vacuum chuck using spinner centering tool and engage chuck vacuum.
a. Spinner requires supply of clean dry air for vacuum to engage.
4.3. Deposit 3 mL of AZ 12XT-20PL-15 photoresist from preprepared syringe onto center of wafer.
a. Ensure there are no air bubbles in resist
4.4. Close lid and run program
a. Spin on 500 RPM for 10 seconds
b. Spin 2000 RPM for 45 seconds
5. EDGE BEAD REMOVAL
1. Remove photoresist edge bead to improve lithographic alignment. See Parylene C Coating Subprotocol.

Prepared by: PIE Foundry | Reviewed by: Kee Scholten | Page 3 of 4
6. SOFT-BAKE
6.1. Bake the wafer on hotplate for 3 minutes at 110 °C. Calibrate temperature to IR gun and do not rely on hotplate reading.
6.2. Wafer should be placed in the center of the hot plate with flat facing forward. Use heat shield around hot plate.
6.3. After baking, store the wafer in black wafer storage box for at least 3 minutes.
7. ALIGN, CONTACT, AND EXPOSURE
7.1. Set the UV lamp to desired intensity and duration. Targeted dose is 117.5 mJ/cm² . Typical
intensity is 12.5 mW/cm²
for 9.4 seconds but can be adjusted depending on current lamp intensity.
7.2. Clean mask aligner vacuum chuck and mask holder of any particles. Remove vacuum O-ring around vacuum chuck if present.
7.3. Place photomask feature (chrome) side down (facing vacuum chuck). Secure with mask holder vacuum and screw clamps.
7.4. Place wafer face up and centered on vacuum chuck. Turn on substrate vacuum.
7.5. Blow mask surface and wafer surface clean of particles with N2 gun.
7.6. Engage N2 purge.
7.7. Lower mask holder.
7.8. Raise wafer using Z-axis knob until mask is flush with mask. Engage ball lock.
7.9. Reduce Z-axis control sensitivity. While looking through aligner microscope on lowest magnification, lower wafer until it just barely disengages with mask. Confirm that wafer is now able to move freely using fine X/Y/θ controls.
7.10. Moving back and forth between left and right alignment marks, align the angle (theta) of the mask and wafer.
7.11. Once wafer and mask are aligned in theta, ensure X and Y coordinates are aligned.
7.12. Increase magnification to higher objective lens then repeat 5.10-5.12.
7.13. Once satisfied, raise the wafer to contact, confirm alignment has not drifted. Disengage N2 purge.
7.14. Expose the wafer by carefully sliding the aligner assembly under the UV lamp. Wait for exposure, then carefully slide the assembly back to starting position.
7.15. Re-engage N2 purge. Gently lower the wafer. If the wafer does not move freely, pause, and wait before trying again.
7.16. Once the wafer moves freely, return Z-axis sensitivity to starting level and lower the wafer completely clear of the mask. Raise the mask holder. Dis-engage substrate vacuum and N2 purge. Remove wafer.
8. POST-EXPOSURE-BAKE
8.1. Bake the wafer on hotplate for 90 seconds at 90 °C. Calibrate temperature to IR gun and do not rely on hotplate reading.
8.2. Wafer should be placed in the center of the hot plate with flat facing forward. Use heat shield around hot plate.
8.3. Allow wafer to cool to room temperature before development.

Prepared by: PIE Foundry | Reviewed by: Kee Scholten | Page 4 of 4
9. DEVELOP
9.1. Develop wafer in shallow bath of 726 MIF developer for approximately 75 seconds.
a. Development time is dependent on area of exposed features and will vary between mask-sets.
9.2. Immediately rinse in DI water bath and rinse 3× in water.
9.3. Blow dry with N2.

10.INSPECT
10.1. Inspect under compound microscope with yellow light filter.

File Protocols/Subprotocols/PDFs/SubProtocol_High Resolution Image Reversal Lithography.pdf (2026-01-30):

Polymer Implantable Electrode Foundry
High Resolution Image Reversal Lithography v. 1.03 | Date: 1/30/2026
Prepared by: PIE Foundry | Reviewed by: Kee Scholten | Page 1 of 4

## Sub-Protocol: High Resolution Image Reversal Lithography

Description: This document details the protocol for the high-resolution image reversal lithography used to produce the lift-off profile for metal patterning in the PIE Foundry standard microfabrication process. It is tailored for use on Parylene C coated silicon wafers.

## MATERIALS

AZ5214-E Photoresist
AZ340 Developer
5 mL Polypropylene Syringe (per wafer) 22-Gauge Luer Stub (per wafer)

## EQUIPMENT

OAI Model 200 Contact Mask Aligner and UV Source
Electronic Micro Systems 1000-1 Hot plate
YES CV200RFS Plasma Asher
Laurell Technologies Photoresist Spinner Model WS-400B-6NPP Lite Vacuum oven with N2
UV intensity meter
IR temperature sensor
Wafer centering tool
HDPE trays for developer and water baths Wafer dipper/holding tool

## PARAMETERS

Spinner Recipe Program P
1st Spin Speed: 500 RPM
1st Spin Time: 10 seconds
1st Spin Acceleration: acceleration level 8 (1088 RPM) 2nd Spin Speed: 4200 RPM
2nd Spin Time: 40 seconds
2nd Spin Acceleration: acceleration level 8 (1088 RPM)

Soft-Bake
Temperature: 110 °C
Time: 60 seconds

1st Exposure
Dose: 42 mJ/cm²
Time: 3.4 seconds
Intensity: 12.5 mW/cm²

Prepared by: PIE Foundry | Reviewed by: Kee Scholten | Page 2 of 4

Image-Reversal Bake
Temperature: 110 °C
Time: 63 seconds

2nd Exposure
Dose: 280 mJ/cm²
Time: 22.4 seconds
Intensity: 12.5 mW/cm²

Develop
Concentration: 1:4 AZ340 developer to deionized water (200 mL total volume) Time: 18 seconds

## PROCESS

1. DESCUM
1.1. Descum (clean/roughen) wafers in the asher using the following recipe: 300 mT, 100 W, 300 seconds
2. PREPARE DEVELOPER AND WATER BATHS
Note: perform in chemical fume hood
2.1. Prepare a shallow HDPE tray full of DI water, and with a 1:4 mixture of AZ340 developer and DI water (200 mL total volume).
a. 200 mL of developer solution should be sufficient for 2 wafers.

### 3. DRY-BAKE

Note: this step should be performed immediately before photoresist deposition
3.1. Bake wafers at 60 °C in an oven under light vacuum (35-40 cmHg) and N¬2 flow (15-20 sccm) for >15 minutes
4. SPIN PHOTORESIST
Note: Before coating wafers run 3 “dummy spins” using spare wafers to ensure spinner chamber environment is saturated with solvent from photoresist. This will prevent differences in resist thickness between first and last wafers in a run.
4.1. Line sidewalls of spinner with aluminum foil to reduce mess.
4.2. Center wafer on spinner vacuum chuck using spinner centering tool and engage chuck vacuum.
a. Spinner requires supply of clean dry air for vacuum to engage.
4.3. Deposit 3 mL of AZ5214-E photoresist from preprepared syringe onto center of wafer through 22-gauge Luer stub.
a. Ensure there are no air bubbles in resist

Prepared by: PIE Foundry | Reviewed by: Kee Scholten | Page 3 of 4
4.4. Close lid and run program
a. Spin on 500 RPM for 10 seconds
b. Spin 4200 RPM for 40 seconds
5. SOFT-BAKE
5.1. Bake the wafer on hotplate for 1 minute at 110 °C. Calibrate temperature to IR gun and do not rely on hotplate reading.
5.2. Wafer should be placed in the center of the hot plate with flat facing forward. Use heat shield around hot plate.
5.3. After baking, store the wafer in black wafer storage box for at least 3 minutes.
6. VACUUM CONTACT AND EXPOSURE
6.1. Set the UV lamp to desired intensity and duration. Targeted dose is 42 mJ/cm² . Typical
intensity is 12.5 mW/cm²
for 3.4 seconds but can be adjusted depending on current lamp intensity.
6.2. Clean mask aligner vacuum chuck and mask holder of any particles. Place vacuum O-ring around vacuum chuck.
6.3. Place photomask feature (chrome) side down (facing vacuum chuck). Secure with mask holder vacuum and screw clamps.
6.4. Place wafer face up and centered on vacuum chuck. Turn on substrate vacuum.
6.5. Blow mask surface and wafer surface clean of particles with N2 gun.
6.6. Engage N2 purge.
6.7. Lower mask holder.
6.8. Raise wafer using Z-axis knob until mask appears flush with mask. Lower mask slightly and then use fine x/y/θ controls to center wafer under mask. Re-raise wafer.
6.9. Turn off substrate vacuum and engage contact vacuum. Open contact vacuum knob until vacuum gauge reads ~5” Hg. You may need to lower N2 purge to create good seal. Please note, sufficient vacuum is only needed to create good contact between mask and wafer as indicated by appearance of Newton ring diffraction. Use the lowest possible vacuum setting that will achieve this effect.
6.10. Expose the wafer by carefully sliding the aligner assembly under the UV lamp. Wait for exposure, then carefully slide the assembly back to starting position.
6.11. Lower the contact vacuum level by turning the knob clockwise. Once closed, turn off the contact vacuum. If the N2 purge level was decreased, return it to starting level. Re-engage the substrate vacuum and then gently lower the wafer. If the wafer does not move freely, pause, and wait before trying again.
6.12. Lower the wafer completely clear of the mask. Raise the mask holder. Dis-engage substrate vacuum and N2 purge. Remove wafer.
7. IMAGE-REVERSAL-BAKE
7.1. Bake the wafer on hotplate for 63 seconds at 110 °C ± 0.5 °C. Calibrate temperature to IR gun and do not rely on hotplate reading.

Prepared by: PIE Foundry | Reviewed by: Kee Scholten | Page 4 of 4
a. This step is critical. Avoid any variation in time or temperature.
7.2. Wafer should be placed in the center of the hot plate with flat facing forward. Use heat shield around hot plate.
7.3. After baking, store the wafer in black wafer storage box for at least 3 minutes.
8. FLOOD EXPOSURE
8.1. Set the UV lamp to desired intensity and duration. Targeted dose is 280 mJ/cm² . Typical
intensity is 12.5 mW/cm²
for 22.4 seconds but can be adjusted depending on current lamp intensity.
8.2. Remove mask from mask holder and store.
8.3. Place wafer face up and centered on vacuum chuck. Turn on substrate vacuum.
8.4. Blow wafer surface clean of particles with N2 gun.
8.5. Expose the wafer by carefully sliding the aligner assembly under the UV lamp. Wait for exposure, then carefully slide the assembly back to starting position.
8.6. . Dis-engage substrate vacuum. Remove wafer.
9. QUENCH IN DEIONIZED WATER
9.1. Immediately place wafer in shallow bath of DI water and let soak for 3 minutes to avoid heating and reduce gas bubble formation.

10.DEVELOP
10.1. Develop wafer in 1:4 solution of AZ340 to DI water for 18 seconds with mild agitation.
10.2. Immediately rinse in DI water bath and rinse 3× in water.
10.3. Blow dry with N2.

11.INSPECT
11.1. Inspect under compound microscope with yellow light filter.

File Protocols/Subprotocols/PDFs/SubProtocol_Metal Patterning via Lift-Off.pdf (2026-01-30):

Polymer Implantable Electrode Foundry
Metal Patterning via Lift-Off v. 1.03 | Date: 01/30/2026
Prepared by: PIE Foundry | Reviewed by: Kee Scholten | Page 1 of 2

## Sub-Protocol: Metal Patterning via Lift-Off

Description: This document details the protocol for the high-resolution image reversal lithography used to produce the lift-off profile for metal patterning in the PIE Foundry standard microfabrication process. It is tailored for use on Parylene C coated silicon wafers.

## MATERIALS

Acetone
Isopropanol (IPA)
N-Methylpyrrolidone (NMP)

## EQUIPMENT

Glass dishes designated for lift-off Sonicating bath
PTFE vertical wafer holder

## PROCESS

1. ACETONE SOAK
Note: Perform all steps in solvent fume hood
Note: Lift-off is a particulate generating process. Expect dishware and tweezers to become contaminated by metal particles. Designated tweezers and glassware for lift-off only processing.
1.1. Soak wafers for at least one hour, and for as long as overnight, in room temperature acetone bath. The shortest possible soak duration should be used. Features should begin to appear after a few minutes. If not, the photoresist profile may be incorrect.
a. Bath will need to be covered in aluminum foil to prevent solvent evaporation overnight.
b. If possible, wafers should be stood vertical to reduce particle redeposition.
2. PREPARE SOLVENT BATHS
2.1. The following day prepare solvent baths in fume hood (organic solvents must be in glass containers marked for liftoff):
a. Room temperature NMP solution in ultrasonic bath
b. Room temperature bath of NMP rinse
c. Room temperature bath of IPA
d. Room temperature bath of DI water

Polymer Implantable Electrode Foundry
Metal Patterning via Lift-Off v. 1.03 | Date: 01/30/2026
Prepared by: PIE Foundry | Reviewed by: Kee Scholten | Page 2 of 2
3. ULTRASONIC BATH
3.1. Transfer wafer from acetone bath to NMP ultrasonic bath. As the wafer is removed from the solvent immediately spray with NMP while holding the wafer at a downward sloping angle to remove all remaining metal flakes. Make all efforts to prevent the wafer from drying.
3.2. Apply ultrasonic for 1-2 minutes
4. SOLVENT RINSE
4.1. Transfer wafer to the NMP rinse. Again, spray vigorously with NMP squeeze bottle while holding the wafer at a downward sloping angle to remove all remaining metal flakes. Let rinse for > 5 minutes.
4.2. Transfer wafer to the IPA rinse. Spray vigorously with NMP squeeze bottle while holding the wafer at a downward sloping angle to remove all remaining metal flakes. Let rinse for > 5 minutes.
4.3. Transfer wafer to the DI rinse. Spray vigorously with IPA squeeze bottle while holding the wafer at a downward sloping angle to remove all remaining metal flakes. Rinse with DI water 3× times.
4.4. Blow dry with N2
5. INSPECT AND CLEAN
5.1. Inspect features under compound microscope.
5.2. Clean up chemicals and dishes
a. Dispose of NMP and IPA in solvent waste bottle
b. Glass dishes should be rinsed clean with acetone, IPA, and DI water

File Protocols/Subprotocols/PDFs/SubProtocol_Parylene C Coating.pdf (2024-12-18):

Polymer Implantable Electrode Foundry
Parylene C Coating | Date: 12/16/202
Prepared by: PIE Foundry | Reviewed by: Kee Scholten | Page 1 of 3

## Sub-Protocol: Parylene C Coating

Description: This document details the protocol for coating silicon wafers (or similar materials) in Parylene C using a room temperature vapor deposition method.

Note: Items not allowed in chamber include wood or wood products, scotch tape, liquids, or any substance likely to off-gas while under vacuum.

### MATERIALS

2% Micro-90 Solution
TexWipe Cloths
Parylene C Dimer
Parafilm
Aluminum Foil (Contaminant-Free/Vacuum Grade) Scotch-Brite Pads

### EQUIPMENT

Specialty Coating Systems PDS 2010 Labcoter 2 Parylene Deposition System FTS Systems Flexi-Cool Mechanical Chiller and Cold Trap Probe
Rotating shelf
Digital scale
Boat form (metal tube)

### PARAMETERS

Vaporizer heater: 175 °C
Pressure set point: Base (as measured during tool calibration) + 15 vacuum units (typically 35) Pyrolysis heater: 690 °C

### PROCESS

### 1. CLEAN AND SETUP (0.5 HOURS) 1.1. Consult log to estimate the amount of Parylene C dimer required for targeted coating

thickness. Most current measurements as of 12/16/2024 suggest 32-34 grams for 10 microns across 12 4” silicon wafers. Dimer mass to thickness ratio is determined by loading of the chamber and will be different for tools using different shelving units.
1.2. Weigh out Parylene C dimer in cleanroom using the scale. Log mass to the tenth of a gram. Seal Parylene C dimer bottle with parafilm.
1.3. Fill out log-sheet. Every 5th run (i.e. runs numbered 5, 10, 15, etc.) consult maintenance schedule, document, and notify super-user.

Prepared by: PIE Foundry | Reviewed by: Kee Scholten | Page 2 of 3
1.4. Check cold-trap, vaporizer door, and chamber lid O-rings to make sure each is clean and will form a good seal. If necessary, clean chamber lid O-ring by using Kapton tape adhesive to remove residue. Replace any cracked or badly fouled O-rings and notify super-user to replace in inventory.

### 1.5. During normal setup and operation, do NOT remove chamber base L-gasket. The gasket

should only be disturbed if the tool is unable to pump down to base vacuum and troubleshooting is required.
1.6. Wipe all interior surfaces of the machine (chamber lid, rotating table, bottom plate, baffle, etc.) and the cold trap probe with a TexWipe cloth wetted with Micro-90 solution. Do not wipe the shelf as this can trap fibers. Thoroughly dry all wiped surfaces.
1.7. Place the Flexi-Cool cold trap probe into the cold trap in the coating system.
1.8. Place the rotating shelf onto the base.
1.9. Place your wafers onto the shelves, flats facing inward. Each shelf can accommodate 2 4” wafers. Ensure no sample extends beyond the edge of the rotating table.
1.10. Carefully lower chamber around shelf and place chamber lid on top of chamber.

### 2. CONSTRUCT DIMER BOAT

2.1. Cut a rectangular piece of aluminum foil 11x4 inches in dimension and curl the foil around the outsider diameter of the boat form (metal tube). Face shiniest side of the foil toward boat form. Fold in the ends of the foil and remove boat from the form.

The dimer boat must be no more than 7.5 inches long.

2.2. Pour the Parylene C dimer pellets into the foil boat and load the boat into the vaporizer.

When loading the boat, place it only as far into the vaporizer tube as necessary and do not push the foil boat towards the back of the vaporizer tube.
2.3. Close and lock the vaporizer door.

### 3. RUN PARYLENE C COATING SYSTEM (MIN. 2 HOURS)

3.1. Twist the “Emergency Stop” button until it pops.
3.2. Push “Main Power” button. Wait until all the controllers on the display panel to activate and display current measurement readings.
3.3. Turn the “Vacuum” knob to “Vacuum”. Initial vacuum reading should be around 1000 units. Press down on the lid for the first 20 seconds to help establish a good seal. The vacuum gauge should reach ~100 units in approximately 2 minutes. If not, there may be a leak, or an offgassing sample.
3.4. Once the vacuum gauge reads below 100 units turn on the chiller. Wait a minimum of 45 minutes from this point before starting the deposition process.
3.5. Wait until the vacuum level has reached 5 units (or lower) AND 45 minutes have elapsed since turning on the chiller. Turn the “Furnace” and “Vaporizer” knobs to “Enable”, and then press the “Process Start/Stop” button. The green button should now be illuminated.

Prepared by: PIE Foundry | Reviewed by: Kee Scholten | Page 3 of 3
3.6. Wait for deposition.

For coating to begin, all the following must occur:
a. The chamber gauge must reach 135 °C.
b. The furnace must reach 690 °C.
c. The vacuum reading must be less than 11.
3.7. If any of these conditions are not met, something is wrong. Abort the run and contact super-user.
3.8. The machine will run for several hours depending on the coating thickness. The run will stop automatically, and the tool will begin to cool down when the process is complete. This will be indicated by a blinking green light on the “Process Start/Stop” button.

### 4. COOL DOWN AND CLEANUP (~1 HOUR)

4.1. Wait until the vaporizer temperature is below 90 °C.
4.2. Turn off the chiller and wait > 5 minutes.
4.3. Press the “Process Start/Stop” button.
4.4. Turn the “Furnace” and “Vaporizer” knobs to “Disable”.
4.5. Turn the “Vacuum: knob to “Vent”. Wait until vacuum gauge reads ~1000 units.
4.6. Push the “Emergency Stop” button to power off coating system.
4.7. Carefully remove the cold trap probe from the system and place in the holder to warm.
4.8. Remove chamber lid.
4.9. Remove and store samples.
4.10. Peel Parylene C from the inside surfaces: chamber, chamber lid, rotating table, bottom plate, watch glass. If the Parylene C film is very thin (<3 microns) leave until the following run.
4.11. Open vaporizer and discard the used foil boat. Remove any Parylene C residue from the outside of the vaporizer tube using a plastic chisel. Clean the inside of the vaporizer tube using the tube brush. Vacuum out any residue.
4.12. Wipe the inside surfaces of the chamber (but not the vaporizer or shelf) with a TexWipe cloth wetted with Micro-90 solution.
4.13. Outside of the cleanroom scrub the cold trap probe completely clean using a green Scotch-Brite pad. Polish with a TexWipe cloth and Micro-90 solution. Any cloudiness or residue will lead to rust spots, which is good for neither the probe nor the pump. Return the chiller and cold trap to the cleanroom.
4.14. Log any issues or observations in the logbook.

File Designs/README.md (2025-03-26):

All mask designs are included in a single DXF file as separate layers (metal, etch layer 1, etch layer2)
- DXF units are microns
- Built in AutoCAD 2022 S.51.0.0

All PDF designs include Eagle files (schematic and boards), as well as most recent Gerber files for production and drawings with dimensions.
- All units including drawing dimensions in mm unless otherwise noted
- Built in Eagle v9.6.2
- Eagle libraries can be found in [Resources](/Resources/Libraries)

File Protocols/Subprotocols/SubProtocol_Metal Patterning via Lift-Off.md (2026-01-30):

# Sub-Protocol: Metal Patterning via Lift-Off

Description: This document details the protocol for the high-resolution image reversal lithography used to produce the lift-off profile for metal patterning in the PIE Foundry standard microfabrication process. It is tailored for use on Parylene C coated silicon wafers.

## Materials:
* *Acetone*
* *Isopropanol (IPA)*
* *N-Methylpyrrolidone (NMP)*

## Equipment:
* *Glass dishes designated for lift-off*
* *Sonicating bath*
* *PTFE vertical wafer holder*

## Process:

1. Acetone Soak <br>_Note: Perform all steps in solvent fume hood_ <br>_Note: Lift-off is a particulate generating process. Expect dishware and tweezers to become contaminated by metal particles. Designated tweezers and glassware for lift-off only processing._
    1. Soak wafers for at least one hour, and for as long as overnight, in room temperature acetone. The shortest possible soak duration should be used.. Features should begin to appear after a few minutes. If not, the photoresist profile may be incorrect
    <br> a. Bath will need to be covered in aluminum foil to prevent solvent evaporation overnight
    <br> b. If possible, wafers should be stood vertical to reduce particle redeposition

2. Prepare Solvent Baths
    1. The following day prepare solvent baths in fume hood (organic solvents must be in glass containers marked for liftoff)
    <br> a. Room temperature NMP solution in ultrasonic bath set
    <br> b. Room temperature bath of NMP rinse
    <br> c. Room temperature bath of IPA
    <br> d. Room temperature bath of DI water

3. Dry-Bake <br> _Note: this step should be performed immediately before photoresist deposition_
    1. Bake wafers at 60 °C in an oven under light vacuum (35-40 cmHg) and N¬2 flow (15-20 sccm) for >15 minutes

4. Ultrasonic Bath
    1. Transfer wafer from acetone bath to NMP ultrasonic bath. As the wafer is removed from the solvent immediately spray with NMP while holding the wafer at a downward sloping angle to remove all remaining metal flakes. Make all efforts to prevent the wafer from drying
    2. Apply ultrasonic for 1-2 minutes

5. Solvent Rinse
    1. Transfer wafer to the NMP rinse. Again, spray vigorously with NMP squeeze bottle while holding the wafer at a downward sloping angle to remove all remaining metal flakes. Let rinse for > 5 minutes
    2. Transfer wafer to the IPA rinse. Spray vigorously with NMP squeeze bottle while holding the wafer at a downward sloping angle to remove all remaining metal flakes. Let rinse for > 5 minutes
    3. Transfer wafer to the DI rinse. Spray vigorously with IPA squeeze bottle while holding the wafer at a downward sloping angle to remove all remaining metal flakes. Rinse with DI water 3× times
    4. Blow dry with N<sub>2</sub>

6. Inspect and Clean
    1. Inspect features under compound microscope
    2. Clean up chemicals and dishes
    <br> a. Dispose of NMP and IPA in solvent waste bottle
    <br> b. Glass dishes should be rinsed clean with acetone, IPA, and DI water

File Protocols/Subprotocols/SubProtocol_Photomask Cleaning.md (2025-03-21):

# Sub-Protocol: Photomask Cleaning

Description: This document details the protocol for the cleaning glass/chromium photomasks. This step is not necessary for freshly manufactured, unused photomasks.

## Materials:
* *Acetone*
* *Isopropanol*
* *Nanostrip*

## Equipment:
* *Glass tank designated for Nanostrip*
* *Hotplate*
* *Teflon mask holder*
* *Mask tweezers*
* *HDPE trays*

## Process:

1. Safety
   1. Nanostrip is very hazardous. Wear acid-resistant gloves, goggles, and chemical apron at a minimum. All work should be conducted in a corrosives fume hood

2. Solvent clean
<br> _Note: perform in chemical fume hood_
   1. Soak the photomask in a shallow acetone bath in a solvent compatible receptacle (HDPE tray labeled for solvent use, or glass tank designated for photoresist stripping). Liberally spray with acetone to remove large debris and significant photoresist residue
   2. Repeat with a shallow bath of isopropanol
   3. Repeat with deionized water
   4. Blow dry with N<sub>2</sub>

3. Nanostrip Clean
<br> _Note: perform in corrosives appropriate fume hood_
   1. Fill the glass Nanostrip tank with a shallow layer of solution, enough to cover the photomask
   2. Place the tank on a hotplate and set to 60 °C. Allow plate to reach temperature
   3. Prepare two HDPE trays with deionized water for rinsing
   4. Place the photomask in the Teflon mask holder chrome/pattern side up
   5. Carefully transfer the mask to the tank still in the holder and let soak for > 10 minutes
   6. Carefully transfer the mask to the first rinsing tray and rinse briefly
   7. Transfer mask to the second tray and rinse 5× with deionized water
   8. Blow dry photomask with N<sub>2</sub>

4. Clean and Dispose of Nanostrip
   1. Turn-off hotplate and allow solution to reach room temperature
   2. While waiting, fully rinse water trays and mask holder and dry thoroughly
   3. When the solution has cooled, decant carefully with aid of glass funnel into labeled glass waste beaker
   4. Triple rinse tank

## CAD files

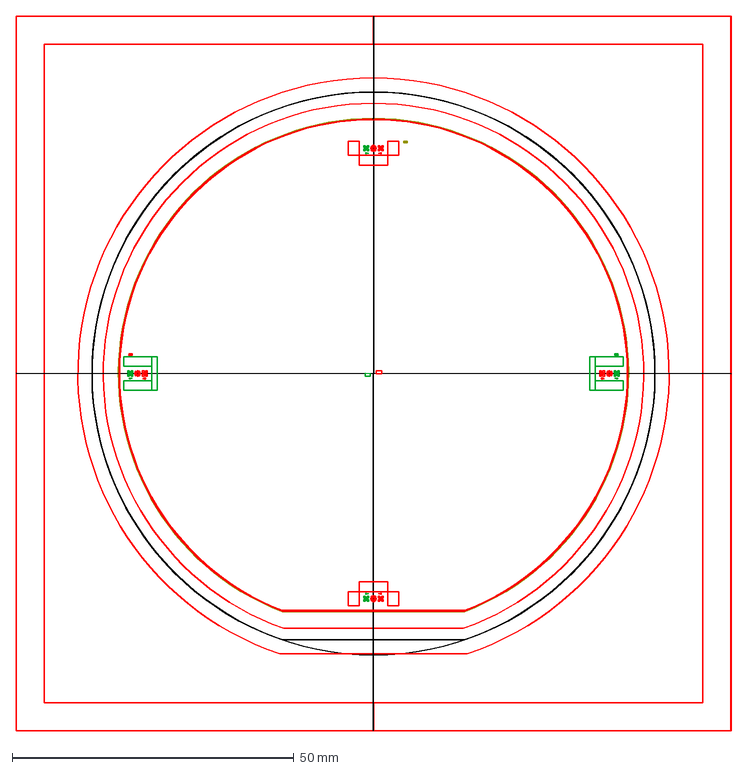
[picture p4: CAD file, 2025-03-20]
Designs/Lithographic Designs/Miscellaneous/MaskTemplate v5.dxf
127.0 x 127.0 mm

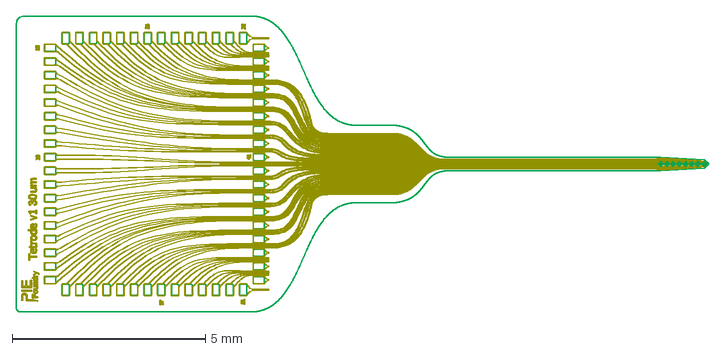
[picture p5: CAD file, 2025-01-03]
Designs/Lithographic Designs/Tetrode Array/Tetrode v1 30micron.dxf
17.9 x 7.65 mm

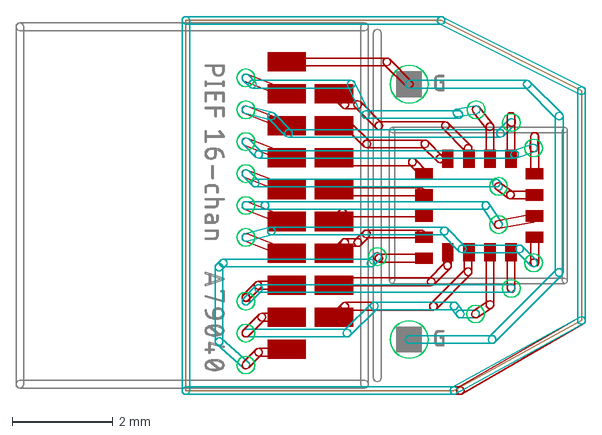
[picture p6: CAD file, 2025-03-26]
Designs/PCB Designs/16 channel EIB/PIEFoundry 16-channel EIB.dxf
11.3 x 7.54 mm

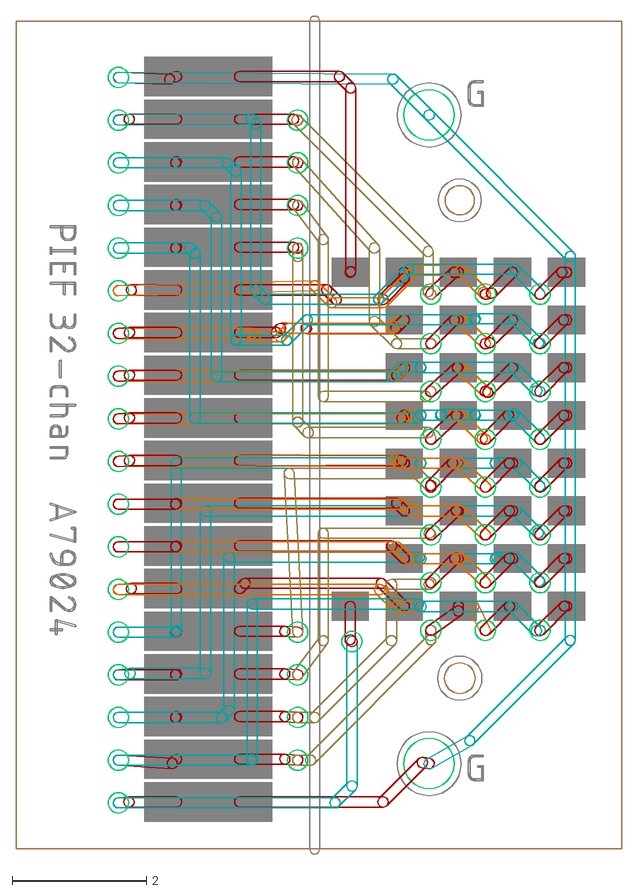
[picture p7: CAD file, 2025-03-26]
Designs/PCB Designs/32 channel EIB/PIEFoundry 32-channel EIB.dxf
9.02 x 12.5

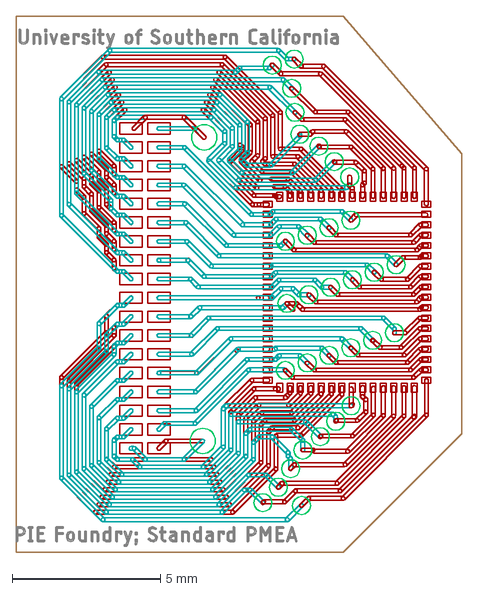
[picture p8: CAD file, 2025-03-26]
Designs/PCB Designs/Standard Array EIB/64 channel Standard Array EIB v1.1.dxf
15.1 x 18.1 mm

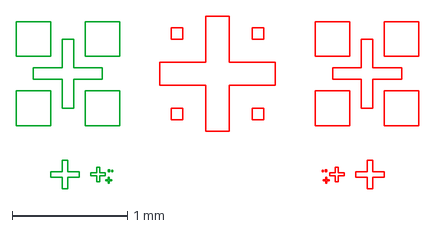
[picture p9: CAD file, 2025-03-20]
Designs/Lithographic Designs/Miscellaneous/Alignment Marks v5.dxf
3.50 x 1.50 mm

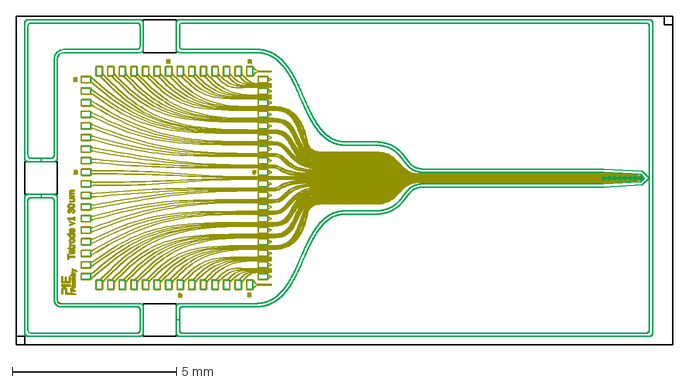
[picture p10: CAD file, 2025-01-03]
Designs/Lithographic Designs/Tetrode Array/Tetrode v1 30micron - MaskSet.dxf
20.0 x 10.0 mm

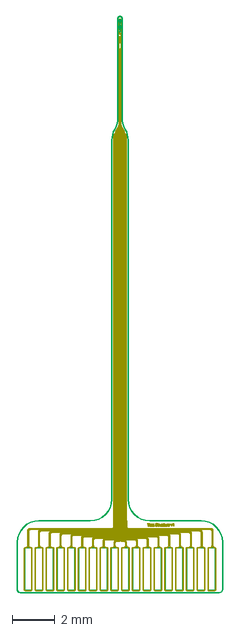
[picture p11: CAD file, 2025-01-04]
Designs/Lithographic Designs/Miscellaneous/Test Structure v1.dxf
9.56 x 26.8 mm

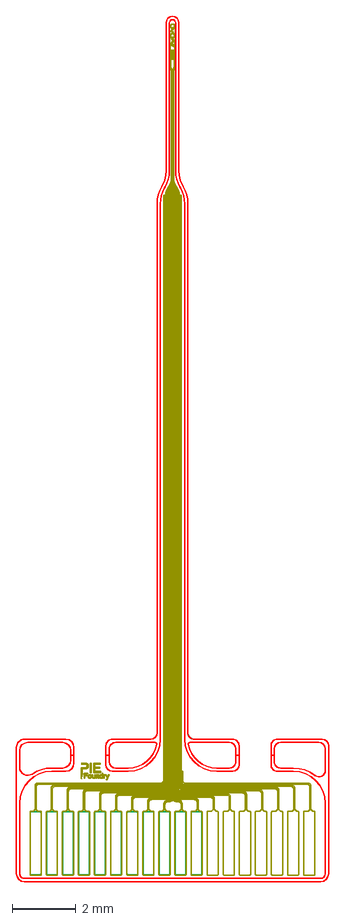
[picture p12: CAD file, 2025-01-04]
Designs/Lithographic Designs/Miscellaneous/Test Structure v1 - MaskSet.dxf
9.76 x 27.1 mm

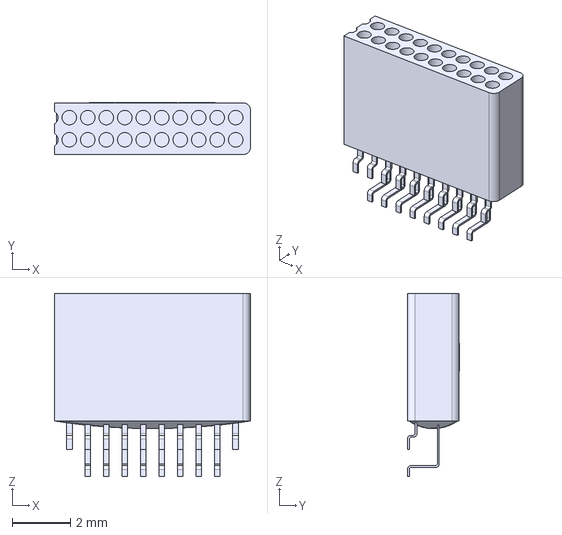
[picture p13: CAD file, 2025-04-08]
Resources/Solids/A79040-001.stp
6.73 x 1.79 x 6.30 mm

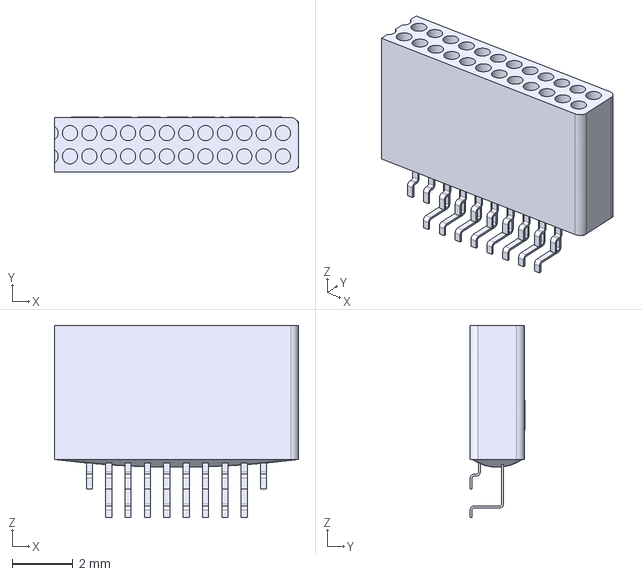
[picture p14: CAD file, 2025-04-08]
Resources/Solids/A79016-001.stp
8.00 x 1.79 x 6.30 mm

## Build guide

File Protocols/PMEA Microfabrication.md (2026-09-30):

# Protocol: Microfabrication of Parylene Microelectrode Arrays

Description: This document details the microfabrication protocol for Parylene microelectrode arrays (MEAs) for the standard multi-project wafer model of the Polymer Implantable Electrode (PIE) Foundry.

_Note: Standard equipment and materials (e.g. tweezers, microscopes, DI water, cleanroom wipes, N<sub>2</sub> gun, scale, etc.) are not listed in materials lists._

Table of Contents

1. [Base Parylene C](#1-base-parylene-c)
   * [Dry-Bake](#11-dry-bake)
   * [Deposit Parylene C](#12-deposit-parylene-c)
   * [Measure Parylene Thickness](#13-measure-parylene-thickness)
   * [Thermal Anneal](#14-thermal-anneal)
2. [Electrode (Metal) Layer](#2-electrode-metal-layer)
   * [Photomask Cleaning](#21-photomask-cleaning)
   * [High Resolution Image Reversal Lithography](#22-high-resolution-image-reversal-lithography)
   * [Descum Wafer](#23-descum-wafer)
   * [Deposit Metal](#24-deposit-metal)
   * [Pattern Metal via Lift-Off](#25-pattern-metal-via-lift-off)
   * [Dry-Bake](#26-dry-bake)
3. [Insulation Parylene C](#3-insulation-parylene-c)
   * [Descum Wafer](#31-descum-wafer)
   * [Silanization](#32-silanization)
   * [Dry-Bake](#33-dry-bake)
   * [Deposit Parylene C](#34-deposit-parylene-c)
   * [Measure Parylene Thickness](#35-measure-parylene-thickness)
4. [Pattern Parylene (Etch #1)](#4-pattern-parylene-etch-1)
   * [Photomask Cleaning](#41-photomask-cleaning)
   * [Pattern Etch Mask with Photolithography](#42-pattern-etch-mask-with-photolithography)
   * [Etch Parylene](#43-etch-parylene)
   * [Strip Photoresist Mask](#44-strip-photoresist-mask)
5. [Pattern Parylene (Etch #2)](#45-dry-bake)
   * [Photomask Cleaning](#5-pattern-parylene-etch-2)
   * [Pattern Etch Mask with Photolithography](#51-photomask-cleaning)
   * [Etch Parylene](#53-etch-parylene)
   * [Strip Photoresist Mask](#54-strip-photoresist-mask)
6. [Release MEAs](#6-release-meas)
7. [Post-Process Annealing](#7-post-process-annealing)
   * [Release Stress (Flatten)](#71-release-stress-flatten)
   * [High Temperature Vacuum Anneal](#72-high-temperature-vacuum-anneal)
   * [Vacuum Anneal](#73-vacuum-anneal)
8. [Post-Process Cleaning](#8-post-process-cleaning)

<ol type="A">
  <li>    <a href="#a-process-flow-diagram">Process Flow Diagram</a>   </li>
  <li>     <a href="#b-material-sources">Material Source</a>   </li>
  <li>     <a href="#c-equipment-models">Equipment Models</a>   </li>
</ol>

## 1. Base Parylene C

### 1.1 Dry-Bake

_Note: this step assumes you are working with new wafers directly taken from the box in which they were shipped in – the assumption is that these wafers are completely clean_

_Note: this step should be performed immediately before Parylene deposition_

Materials:
* *4” prime double-sided-polished 525 micron thick silicon wafer(s) (laser serial marked preferred)*

Equipment:
* *Oven or hotplate*

Process:
1. Bake wafers at 110 °C in an oven at atmosphere for at least 30 minutes (overnight is OK), or on a hot plate for >5 minutes

### 1.2 Deposit Parylene C

_Note: this step should be performed immediately after dry-bake (step 1.1)_

Materials:
* *Parylene C Dimer*

Equipment:
* *Parylene PVD*

Process:
1. Deposit 10 microns of Parylene C on to wafers. [See Parylene C Coating Subprotocol](Subprotocols/SubProtocol_Parylene%20C%20Coating.md).
    1. 30-36 g of dimer is typical, but amount should be verified by comparing to past Parylene runs and adjusted as needed
    2. 12 wafers per batch is recommended and varying the wafer number will affect the amount of dimer required

### 1.3 Measure Parylene Thickness

Equipment:
* *Thin-film thickness measurement system*

Process: 
1. Measure Parylene thickness at center of wafer using non-contact optical profilometer
    1. As an alternative, glass reference slides can be coated alongside each Parylene C wafer shelf. Sections of the Parylene C coating on these slides can be removed by way of a sharp blade, and the reference slide coating thickness measured directly using a contact profilometer. Please note that this method is less accurate.
2. Log measurements into logbook

### 1.4 Thermal Anneal

Equipment:
* *Vacuum oven*

Process:
1. Anneal all wafers with base Parylene C at 150 °C under hard vacuum with a soak time of 4 hours. The purpose of the step is to improve thermal properties of the Parylene C prior to metal evaporation, and to improve adhesion of the Parylene C base to the carrier wafer prior to lithography in Step 2.

## 2. Electrode (Metal) Layer

### 2.1 Photomask Cleaning

_Note: This step should be skipped for newly purchased photomasks which have been first opened under cleanroom conditions_

_Safety: Use acid-resistant gloves, apron, and googles when using Nanostrip_

Materials:
* *Acetone*
* *Isopropanol*
* *Nanostrip*

Equipment:
* *Glass tank designated for Nanostrip*
* *Hotplate*
* *Mask tweezers*
* *Teflon mask holder*

Process:
1. Clean photomask prior to lithography. [See Photomask Cleaning Subprotocol](Subprotocols/SubProtocol_Photomask%20Cleaning.md).

### 2.2 High Resolution Image Reversal Lithography

Materials:
* *5214-E Photoresist*
* *AZ340 Developer*
* *5 mL Polypropylene Syringe (per wafer)*
* *22-Gauge Luer Stub (per wafer)*

Equipment:
* *Vacuum oven with N<sub>2</sub>*
* *Contact mask aligner with UV source*
* *Photoresist spinner*
* *Hot plate*
* *IR temperature sensor*
* *UV intensity meter*
* *Wafer centering tool*
* *HDPE trays for developer and water baths*
* *Wafer dipper/holding tool*
* *Contact profilometer*

Process:
1. Prepare an image reversal photoresist mask of the electrodes, traces, and contact pads. [See High Resolution Image Reversal Lithography Subprotocol](Subprotocols/SubProtocol_High%20Resolution%20Image%20Reversal%20Lithography.md).
2. Confirm and record the thickness of the photoresist with contact profilometer. Target is 1.1 ± 0.5 micron.

### 2.3 Descum Wafer

_Note: this step should be performed immediately before metal deposition_

Equipment:
* *RIE*

Process:
1. Descum (clean) wafers in the RIE, two 4” wafers at the same time, using the following recipe:  
    150 mT, 100 W, 50 sccm O<sub>2</sub>, 90 s.

### 2.4 Deposit Metal

_Note: this step should be performed immediately after descum_

Materials:
* *Titanium*
* *Platinum*
* *Gold*

Equipment:
* *E-beam evaporator*

Process:
1. Before loading metal ensure evaporator chamber and, importantly, the wafer holder, is clean.
2. Coat the wafers in a layer of evaporated metal using e-beam evaporation.
    1. Metal stack and parameters:  
        20 nm Ti (2 Å/s)  
        25 nm Pt (2 Å/s)  
        155 nm Au (3 Å/s)  
        25 nm Pt (2 Å/s)

### 2.5 Pattern Metal via Lift-Off

Materials:
* *Acetone*
* *N-Methylpyrrolidone (NMP)*
* *Isopropanol*

Equipment:
* *Glass dishes designated for lift-off*
* *Sonicating bath*

Process:
1. Lift-off photoresist to reveal metal pattern. [See Metal Patterning via Lift-Off Subprotocol](Subprotocols/SubProtocol_Metal%20Patterning%20via%20Lift-Off.md).

### 2.6 Dry-Bake

_Note: this step should be performed immediately before Parylene C_

Equipment:
* *Vacuum oven with N<sub>2</sub>*

Process:
1. Bake wafers at 60 °C in an oven under light vacuum (35-40 cmHg) and N­<sub>2</sub> flow (15-20 sccm) for >15 minutes

## 3. Insulation Parylene C

### 3.1 Descum Wafer

Equipment:
* *Asher*

Process:
1. Descum (clean) wafers in the asher using the following recipe:  
    300 mT, 10 W, 115 sccm O<sub>2</sub>, 300 s

### 3.2 Silanization

_Note: this step should be performed within 12 hours of Parylene deposition_

Materials:
* *A-174 Silane*
* *Isopropanol*
* *Aluminum foil*

Equipment:
* *Glass dishes designated for A-174*
* *Crystalizing dish labeled for A-174*
* *Wafer cassette designated for A-174*
* *Stirring rod*

Process:
1. Treat the wafers with a solution of A-174 silane to improve adhesion to the insulating Parylene C layer. [See Silanization Subprotocol](Subprotocols/SubProtocol_Silanization.md).

### 3.3 Dry-Bake

_Note: this step should be performed immediately before Parylene C_

Equipment:
* *Vacuum oven with N<sub>2</sub>*

Process:
1. Bake wafers at 60 °C in an oven under light vacuum (35-40 cmHg) and N­<sub>2</sub> flow (15-20 sccm) for >15 minutes

### 3.4 Deposit Parylene C

_Note: this step should be performed within 12 hours after silanization_

Materials:
* *Parylene C Dimer*

Equipment:
* *Parylene PVD*

Process:
1. Deposit 10 microns of Parylene C on to wafers. [See Parylene C Deposition Protocol](Subprotocols/SubProtocol_Parylene%20C%20Coating.md).
    1. 30-36 g of dimer is typical, but amount should be verified by comparing to past Parylene runs and adjusted as needed
    2. 12 wafers per batch is recommended and varying the wafer number will affect the amount of dimer required

### 3.5 Measure Parylene Thickness

Equipment:
* *Thin-film thickness measurement system*

Process:
1. Measure Parylene thickness at center of wafer using non-contact optical profilometer
    1. As an alternative, glass reference slides can be coated alongside each Parylene C wafer shelf. Sections of the Parylene C coating on these slides can be removed by way of a sharp blade, and the reference slide coating thickness measured directly using a contact profilometer. Please note that this method is less accurate.
2. Log measurements into logbook

## 4. Pattern Parylene (Etch #1)

### 4.1 Photomask Cleaning

_Note: This step should be skipped for newly purchased photomasks which have been first opened under cleanroom conditions_

_Safety: Use acid-resistant gloves, apron, and googles when using Nanostrip_

Materials:
* *Acetone*
* *Isopropanol*
* *Nanostrip*

Equipment:
* *Glass tank designated for Nanostrip*
* *Hotplate*
* *Mask tweezers*
* *Teflon mask holder*

Process:
1. Clean photomask prior to lithography. [See Photomask Cleaning Subprotocol](Subprotocols/SubProtocol_Photomask%20Cleaning.md).

### 4.2 Pattern Etch Mask with Photolithography

Materials:
* *12xt-20pl-15 photoresist*
* *MIF 726 developer*

Equipment:
* *Contact mask aligner*
* *Photoresist spinner*
* *Hot plate*
* *IR temperature sensor*
* *Wafer centering tool*

Process:
1. Prepare a photoresist etch mask, approximately 15 microns thick, defining the outline of the MEA, and the openings over the electrodes and contact pads. [See Etch Mask Lithography Protocol](Subprotocols/SubProtocol_Etch%20Mask%20Lithography.md).
2. Confirm and record the thickness of the photoresist with contact profilometer. Target is 15 ± 1 micron.

### 4.3 Etch Parylene

Equipment:
* *RIE-ICP or RIE*

Process:
1. Etch through approximately 10 microns of Parylene C using O<sub>2</sub> plasma using either deep reactive ion etch (DRIE) or reactive ion etch (RIE).
2. DRIE (preferred): A two-step switch-chemistry Bosch-type etch process using an ICP-RIE etching tool. Etch approximately 100-110 cycles in batches of 60 cycles or fewer, with wafers vented and cooled to room temperature between batches.
    1. Etch step:  
        Gas: 60 sccm O<sub>2</sub>, 40 sccm Ar  
        RF Power: 20 W  
        ICP Power: 700 W  
        Time: 10 seconds
    2. Passivation step:  
        Gas: 35 sccm C<sub>4</sub>F<sub>8</sub>, 40 sccm Ar  
        RF Power: 10 W  
        ICP Power: 700 W  
        Time: 3 seconds
    3. Etch rate: approximately 0.095 microns per loop
3. RIE (alternative): A single step O<sub>2</sub> RIE process. Two 4” wafers run side-by-side on a 10” platen.
    1. Gas: 50 sccm O<sub>2</sub>  
        RF Power: 150 W  
        Time: 50 minutes
    2. Etch rate: approximately 0.19 microns per minute.

### 4.4 Strip Photoresist Mask

Materials:
* *Acetone*
* *Isopropanol*

Equipment:
* *Glass dishes designated for photoresist stripping*
* *Solvent fume hood*

Process:
1. Perform chemical work in solvents fume hood
2. Soak wafer in acetone bath for 5 minutes.
3. Soak wafer in isopropanol bath for 5 minutes.
4. Soak in DI water for 5 minutes.
    1. 3× rinse in DI water
5. Blow dry with N<sub>2</sub>

### 4.5 Dry-Bake

_Note: this step should be performed immediately before Parylene C_

Equipment:
* *Vacuum oven with N<sub>2</sub>*

Process:
1. Bake wafers at 60 °C in an oven under light vacuum (35-40 cmHg) and N­<sub>2</sub> flow (15-20 sccm) for >15 minutes

## 5. Pattern Parylene (Etch #2)

### 5.1 Photomask Cleaning

_Note: This step should be skipped for newly purchased photomasks which have been first opened under cleanroom conditions_

_Safety: Use acid-resistant gloves, apron, and googles when using Nanostrip_

Materials:
* *Acetone*
* *Isopropanol*
* *Nanostrip*

Equipment:
* *Glass tank designated for Nanostrip*
* *Hotplate*
* *Mask tweezers*
* *Teflon mask holder*

Process:
1. Clean photomask prior to lithography. [See Photomask Cleaning Subprotocol](Subprotocols/SubProtocol_Photomask%20Cleaning.md).

### 5.2 Pattern Etch Mask with Photolithography

Materials:
* *12xt-20pl-15 photoresist*
* *MIF 726 developer*

Equipment:
* *Contact mask aligner*
* *Photoresist spinner*
* *Hot plate*
* *IR temperature sensor*
* *Wafer centering tool*

Process:
1. Prepare a photoresist etch mask, approximately 15 microns thick, defining the outline of the MEA, and the openings over the electrodes and contact pads. [See Etch Mask Lithography Protocol](Subprotocols/SubProtocol_Etch%20Mask%20Lithography.md).
2. Confirm and record the thickness of the photoresist with contact profilometer. Target is 15 ± 1 micron.

### 5.3 Etch Parylene

Equipment:
* *RIE-ICP or RIE*

Process:
1. Etch through approximately 10 microns of Parylene C using O<sub>2</sub> plasma using either deep reactive ion etch (DRIE) or reactive ion etch (RIE).
    1. DRIE (preferred): A two-step switch-chemistry Bosch-type etch process using an ICP-RIE etching tool. Etch approximately 100-110 cycles without venting in between the process.
    2. Etch step:  
        Gas: 60 sccm O<sub>2</sub>, 40 sccm Ar  
        RF Power: 20 W  
        ICP Power: 700 W  
        Time: 10 seconds
    3. Passivation step:  
        Gas: 35 sccm C<sub>4</sub>F<sub>8</sub>, 40 sccm Ar  
        RF Power: 10 W  
        ICP Power: 700 W  
        Time: 3 seconds
    4. Etch rate: approximately 0.095 microns per loop
2. RIE (alternative): A single step O<sub>2</sub> RIE process. Two 4” wafers run side-by-side on a 10” platen.
    1. Gas: 50 sccm O<sub>2</sub>  
        RF Power: 150 W  
        Time: 50 minutes
    2. Etch rate: approximately 0.19 microns per minute.

### 5.4 Strip Photoresist Mask

_Note: Parylene C dies may begin to lift off from wafer during this step._

Materials:
* *Acetone*
* *Isopropanol*

Equipment:
* *Glass dishes designated for photoresist stripping*

Process:
1. Perform chemical work in solvents fume hood
2. Soak wafer in acetone bath for 5 minutes.
3. Soak wafer in isopropanol bath for 5 minutes.
4. Soak in DI water briefly (<2 minutes)
5. Carefully blow dry if possible

## 6. Release MEAs

_Note: Parylene C MEAs often curl following release due to inter-layer stress._

Equipment:
* *X-acto knife*
* *Miconeedles*
* *Sharp tweezers*
* *Stereoscope*

Process:
1. To remove a tabulated sheet:
    1. Place a droplet of water at the sheet edge.
    2. Looking through a stereoscope, use a scalpel or microneedle to gently lift the edge of the device, allowing the water to wick between the Parylene and the wafer
    3. If needed, tug very gently at the edge of the sheet or along a handling tab using tweezers.
        1. Add more water as needed

## 7. Post-Process Annealing

### 7.1 Release Stress (Flatten)

Materials:
* *Ceramic plates*
* *Isopropanol*

Equipment:
* *Hot plate*

Process:
1. Lay released MEAs flat on a ceramic plate. A few drops of isopropanol may help pull MEAs flat using surface tension.
2. Cover with second ceramic plate and place on hot plate.
3. Set hot plate to 115 °C. Wait 15 minutes after the hot plate has reached temperature and return to < 60 °C temperature. Allow plates and MEAs to cool on hot plate.

### 7.2 High Temperature Vacuum Anneal

Materials:
* *Ceramic plates*

Equipment:
* *Vacuum oven capable of reaching > 200 °C*

Process:
1. Sandwich released MEAs between clean ceramic plates and place in vacuum oven
2. Pump down vacuum oven.
3. Anneal 275 °C with a soak time of 5 hours.

### 7.3 Vacuum Anneal

Materials:
* *Ceramic plates*

Equipment:
* *Vacuum oven with N<sub>2</sub>*

Process:
1. Sandwich released MEAs between clean ceramic plates and place in vacuum oven
2. Pump down vacuum oven, then rinse 3× with N<sub>2</sub>.
3. Anneal 200 °C with a soak time of 48 hours, and a ramp up/down time of 8 hours.

## 8. Post-Process Cleaning

_Note: this step is recommended to remove any remaining scum on electrode sites and improve impedance values_

Materials:
* *Ceramic plates or glass plates/wafers*
* *Kapton tape*

Equipment:
* *Asher*

Process:
1. Attach released devices to a clean carrier wafer (Si or glass) with the electrode sites exposed using small pieces of Kapton tape
2. Clean devices in the Asher using the following recipe:  
    300 mT, 100 W, 115 sccm O<sub>2</sub>, 300 seconds
   
## A. Process Flow Diagram

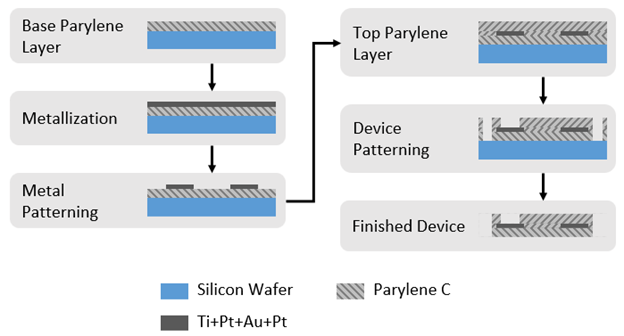
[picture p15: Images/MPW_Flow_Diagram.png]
A diagram of a device pattern


## B. Material Sources

_Note: Standard materials (e.g. acetone, DI water, cleanroom wipes, etc.) are not listed_

| **Material** | **Supplier** |
| --- | --- |
| Parylene dimer | Specialty Coating Systems, Indianapolis, IN |
| AZ 12XT-20PL-15 photoresist | AZ Electronic Materials, Branchburg, NJ |
| AZ 5214 E photoresist | AZ Electronic Materials, Branchburg, NJ |
| AZ 340 developer | AZ Electronic Materials, Branchburg, NJ |
| AZ 726MIF developer | AZ Electronic Materials, Branchburg, NJ |
| Edge Bead Removal (EBR) solvent | AZ Electronic Materials, Branchburg, NJ |
| NMP Rinse | AZ Electronic Materials, Branchburg, NJ |
| Titanium | Provided by USC cleanroom |
| Platinum | Provided by USC cleanroom |
| Gold | Provided by USC cleanroom |
| Nanostrip 2X | CMC Materials, Santa Ana, CA |

## C. Equipment Models

_Note: Standard equipment (e.g. tweezers, microscopes, N<sub>2</sub> gun, scale, etc.) are not listed_

| **Equipment** | **Model #** | **Supplier** |
| --- | --- | --- |
| Vacuum oven with N<sub>2</sub> | TVO-2 | Cascade Tek Inc., Longmont, CO |
| | VO914A | Lindberg/Blue M, New Columbia, PA |
| Profilometer | DektakXT | Bruker, Billerica, MA |
| Spin coater | WS-400B-6NPP Lite | Laurell Technologies, North Wales, PA |
| Hot plate | PMC 730 Dataplate | Barnstead/Thermolyne, Dubuque, IA |
| | 1000-1 | Electronic Micro Systems, Sutton Coldfield, UK |
| Sonicating bath | 3510 | Branson Ultrasonics, Danbury, CT |
| DRIE | Plasmalab 100 | Oxford Instruments, Bristol, UK |
| RIE | PlasmaPro 80 | Oxford Instruments, Bristol, UK |
| | Series 85 | Technics, Pleasanton, CA |
| Asher | CV200RFS | Yield Engineering Systems, Fremont, CA |
| Mask aligner | Model 200 | OAI, San Jose, CA |
| E-beam evaporator | Mark 40 | CHA Industries, Livermore, CA |
| | PRO Line PVD 75 | Kurt J. Lesker, Jefferson Hills, PA |
| Parylene PVD | PDS 2010 Labcoter | Specialty Coating Systems, Indianapolis, IN |

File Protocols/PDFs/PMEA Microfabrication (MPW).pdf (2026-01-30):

Polymer Implantable Electrode Foundry
Microfabrication of Parylene Microelectrode Arrays v. 1.03 | Date: 01/30/2026
Prepared by: PIE Foundry | Reviewed by: Kee Scholten | Page 1 of 12

## Protocol: Microfabrication of Parylene Microelectrode Arrays

Description: This document details the microfabrication protocol for Parylene microelectrode arrays (MEAs) for the standard multi-project wafer model of the Polymer Implantable Electrode (PIE) Foundry.

Note: Standard equipment and materials (e.g. tweezers, microscopes, DI water, cleanroom wipes, N2 gun, scale, etc.) are not listed in materials lists.

## Table of Contents

Prepared by: PIE Foundry | Reviewed by: Kee Scholten | Page 2 of 12

## 1 BASE PARYLENE C

### 1.1 DRY-BAKE

Note: this step assumes you are working with new wafers directly taken from the box in which they were shipped in – the assumption is that these wafers are completely clean
Note: this step should be performed immediately before Parylene deposition
Materials: | 4” prime double-sided-polished 525 micron thick silicon wafer(s) (laser serial marked
| preferred)
Equipment: | Oven or hot plate
1. Bake wafers at 110 °C in an oven at atmosphere for at least 30 minutes (overnight is OK), or on a hot plate for >5 minutes

1.2 DEPOSIT PARYLENE C
Note: this step should be performed immediately after dry-bake (step 1.1)
Materials: | Parylene C dimer
Equipment: | Parylene PVD
1. Deposit 10 microns of Parylene C on to wafers. See Parylene C Coating Subprotocol.
a. 30-36 g of dimer is typical, but amount should be verified by comparing to past Parylene
| runs and adjusted as needed
b. 12 wafers per batch is recommended and varying the wafer number will affect the
| amount of dimer required
c. An optional ~3 g dummy-run can be performed immediately prior to the deposition. For
| a dummy-run the chamber should be empty. This can help trap errant particles which
| can interfere with a uniform coating.

Prepared by: PIE Foundry | Reviewed by: Kee Scholten | Page 3 of 12

1.3 MEASURE PARYLENE THICKNESS
Equipment: Thin film thickness measurement system
1. Measure Parylene thickness at center of wafer using non-contact optical profilometer
a. As an alternative, glass reference slides can be coated alongside each Parylene C wafer
| shelf. Sections of the Parylene C coating on these slides can be removed by way of a sharp blade, and the reference slide coating thickness measured directly using a contact profilometer. Please note that this method is less accurate.
2. Log measurements into logbook

1.4 THERMAL ANNEAL
Equipment: Vacuum oven
1. Anneal all wafers with base Parylene C at 150 °C under hard vacuum with a soak time of 4 hours. The purpose of the step is to improve thermal properties of the Parylene C prior to metal evaporation, and to improve adhesion of the Parylene C base to the carrier wafer prior to lithography in Step 2.

## 2 ELECTRODE (METAL) LAYER

2.1 PHOTOMASK CLEANING
Note: This step should be skipped for newly purchased photomasks which have been first opened under cleanroom conditions
Safety: | Use acid-resistant gloves, apron, and googles when using Nanostrip
Materials: | Acetone
| Isopropanol
| Nanostrip
Equipment: | Glass tank designated for Nanostrip
| Hotplate
| Mask tweezers
| Teflon mask holder
1. Clean photomask prior to lithography. See Photomask Cleaning Subprotocol.

2.2 HIGH RESOLUTION IMAGE REVERSAL LITHOGRAPHY
Materials: | 5214-E Photoresist
| AZ340 Developer
| 5 mL Polypropylene Syringe (per wafer)
| 22-Gauge Luer Stub (per wafer)
Equipment: | Vacuum oven with N2
| Contact mask aligner with UV source
| Photoresist spinner
| Hot plate
| IR temperature sensor
| UV intensity meter

Prepared by: PIE Foundry | Reviewed by: Kee Scholten | Page 4 of 12

IR temperature sensor
Wafer centering tool
HDPE trays for developer and water baths Wafer dipper/holding tool
Contact profilometer
1. Prepare an image reversal photoresist mask of the electrodes, traces, and contact pads. See High Resolution Image Reversal Lithography Subprotocol.
2. Confirm and record the thickness of the photoresist with contact profilometer. Target is 1.1 ± 0.5 micron.

2.3 DESCUM WAFER
Note: this step should be performed immediately before metal deposition
Equipment: RIE
1. Descum (clean) wafers in the RIE, two 4” wafers at the same time, using the following recipe: 150 mT, 100 W, 50 sccm O2, 90 s.

2.4 DEPOSIT METAL
Note: this step should be performed immediately after descum
Materials: | Titanium
| Platinum
| Gold
Equipment: | E-beam evaporator
1. Before loading metal ensure evaporator chamber and, importantly, the wafer holder, is clean.
2. Coat the wafers in a layer of evaporated metal using e-beam evaporation.
a. Metal stack and parameters:
| 20 nm Ti (2 Å/s)
| 25 nm Pt (2 Å/s)
| 155 nm Au (3 Å/s)
| 25 nm Pt (2 Å/s)

2.5 PATTERN METAL VIA LIFT-OFF
Materials: | Acetone
| N-Methylpyrrolidone (NMP)
| Isopropanol (IPA)
Equipment: | Glass dishes designated for lift-off
| Sonicating bath
1. Lift-off photoresist to reveal metal pattern. See Metal Patterning via Lift-Off Subprotocol.

### 2.6 DRY-BAKE

Note: this step should be performed immediately before Parylene C
Equipment: Vacuum oven with N2

Prepared by: PIE Foundry | Reviewed by: Kee Scholten | Page 5 of 12
1. Bake wafers at 60 °C in an oven under light vacuum (35-40 cmHg) and N2 flow (15-20 sccm) for >15 minutes

## 3 INSULATION PARYLENE C

3.1 DESCUM WAFER
Equipment: Asher
1. Descum (clean) wafers in the asher using the following recipe: 300 mT, 115 sccm, 100 W, 300 s

3.2 SILANIZATION
Note: this step should be performed within 12 hours of Parylene deposition
Materials: | A-174 Silane
| Isopropanol
| Aluminum foil
Equipment: | Glass dishes designated for A-174
| Crystalizing dish labeled for A-174
| Wafer cassette designated for A-174
| Stirring rod
1. Treat the wafers with a solution of A-174 silane to improve adhesion to the insulating Parylene C layer. See Silanization Subprotocol.

### 3.3 DRY-BAKE

Note: this step should be performed immediately before Parylene C
Equipment: Vacuum oven with N2
2. Bake wafers at 60 °C in an oven under light vacuum (35-40 cmHg) and N2 flow (15-20 sccm) for >15 minutes

3.4 DEPOSIT PARYLENE C
Note: this step should be performed within 12 hours after silanization
Materials: | Parylene C dimer
Equipment: | Parylene PVD
1. Deposit 10 microns of Parylene C on to wafers. See Parylene C Deposition Protocol.
a. 30-36 g of dimer is typical, but amount should be verified by comparing to past Parylene
| runs and adjusted as needed
b. 12 wafers per batch is recommended and varying the wafer number will affect the
| amount of dimer required
c. An optional ~3 g dummy-run can be performed immediately prior to the deposition. For
| a dummy-run the chamber should be empty. This can help trap errant particles which
| can interfere with a uniform coating.

Prepared by: PIE Foundry | Reviewed by: Kee Scholten | Page 6 of 12

3.5 MEASURE PARYLENE THICKNESS
Equipment: Thin film thickness measurement system
1. Measure Parylene thickness at center of wafer using non-contact optical profilometer
a. As an alternative, glass reference slides can be coated alongside each Parylene C wafer
| shelf. Sections of the Parylene C coating on these slides can be removed by way of a sharp blade, and the reference slide coating thickness measured directly using a contact profilometer. Please note that this method is less accurate.
2. Log measurements into logbook

## 4 PATTERN PARYLENE (ETCH #1)

4.1 PHOTOMASK CLEANING
Note: This step should be skipped for newly purchased photomasks which have been first opened under cleanroom conditions
Safety: | Use acid-resistant gloves, apron, and googles when using Nanostrip
Materials: | Acetone
| Isopropanol
| Nanostrip
Equipment: | Glass tank designated for Nanostrip
| Hotplate
| Mask tweezers
| Teflon mask holder
1. Clean photomask prior to lithography. See Photomask Cleaning Subprotocol.

4.2 PATTERN ETCH MASK WITH PHOTOLITHOGRAPHY
Materials: | 12XT-20PL-15 photoresist
| MIF 726 developer
Equipment: | Contact mask aligner with UV source
| Photoresist spinner
| Hot plate
| IR temperature sensor
| Wafer centering tool
1. Prepare a photoresist etch mask, approximately 15 microns thick, defining the outline of the MEA, and the openings over the electrodes and contact pads. See Etch Mask Lithography Protocol.
2. Confirm and record the thickness of the photoresist with contact profilometer. Target is 15 ± 1 micron.

4.3 ETCH PARYLENE
Equipment: RIE-ICP or RIE
1. Etch through approximately 10 microns of Parylene C using O2 plasma using either deep reactive ion etch (DRIE) or reactive ion etch (RIE).

Prepared by: PIE Foundry | Reviewed by: Kee Scholten | Page 7 of 12
2. DRIE (preferred): A two-step switch-chemistry Bosch-type etch process using an ICP-RIE etching tool. Etch approximately 100-110 cycles in batches of 60 cycles or fewer, with wafers vented and cooled to room temperature between batches. Ensure platten chiller is on and set to 20 C.
a. Etch step:
Gas: 60 sccm O2, 40 sccm Ar
RF Power: 20 W
ICP Power: 700 W
Time: 10 seconds
b. Passivation step:
Gas: 35 sccm C4F8, 40 sccm Ar RF Power: 10 W
ICP Power: 700 W
Time: 3 seconds
c. Etch rate: approximately 0.095 microns per loop
3. RIE (alternative): A single step O2 RIE process. Two 4” wafers run side-by-side on a 10” platen.
a. Gas: 50 sccm O2
RF Power: 150 W
Time: 50 minutes
b. Etch rate: approximately 0.19 microns per minute.

4.4 STRIP PHOTORESIST MASK
Materials: | Acetone
| Isopropanol (IPA)
Equipment: | Glass dishes designated for photoresist stripping
| Solvent fume hood
1. Perform chemical work in solvents fume hood
2. Soak wafer in acetone bath for 5 minutes.
3. Soak wafer in isopropanol bath for 5 minutes.
4. Soak in DI water for 5 minutes.
a. 3× rinse in DI water
5. Blow dry with N2

### 4.5 DRY-BAKE

Note: this step should be performed immediately before Parylene C
Equipment: Vacuum oven with N2
1. Bake wafers at 60 °C in an oven under light vacuum (35-40 cmHg) and N2 flow (15-20 sccm) for >15 minutes

Prepared by: PIE Foundry | Reviewed by: Kee Scholten | Page 8 of 12

## 5 PATTERN PARYLENE (ETCH #2)

5.1 PHOTOMASK CLEANING
Note: This step should be skipped for newly purchased photomasks which have been first opened under cleanroom conditions
Safety: | Use acid-resistant gloves, apron, and googles when using Nanostrip
Materials: | Acetone
| Isopropanol
| Nanostrip
Equipment: | Glass tank designated for Nanostrip
| Hotplate
| Mask tweezers
| Teflon mask holder
1. Clean photomask prior to lithography. See Photomask Cleaning Subprotocol.

5.2 PATTERN ETCH MASK WITH PHOTOLITHOGRAPHY
Materials: | 12XT-20PL-15 photoresist
| MIF 726 developer
Equipment: | Contact mask aligner with UV source
| Photoresist spinner
| Hot plate
| IR temperature sensor
| Wafer centering tool
1. Prepare a photoresist etch mask, approximately 15 microns thick, defining the outline of the MEA, and the openings over the electrodes and contact pads. See Etch Mask Lithography Protocol.
2. Confirm and record the thickness of the photoresist with contact profilometer. Target is 15 ± 1 micron.

5.3 ETCH PARYLENE
Equipment: RIE-ICP or RIE
1. Etch through approximately 10 microns of Parylene C using O2 plasma using either deep reactive ion etch (DRIE) or reactive ion etch (RIE).
a. DRIE (preferred): A two-step switch-chemistry Bosch-type etch process using an ICP-RIE
| etching tool. Etch approximately 100-110 cycles without venting in between the
| process. Ensure platten chiller is on and set to 20 C.
b. Etch step:
| Gas: 60 sccm O2, 40 sccm Ar
| RF Power: 20 W
| ICP Power: 700 W
| Time: 10 seconds

Prepared by: PIE Foundry | Reviewed by: Kee Scholten | Page 9 of 12
c. Passivation step:
Gas: 35 sccm C4F8, 40 sccm Ar RF Power: 10 W
ICP Power: 700 W
Time: 3 seconds
d. Etch rate: approximately 0.095 microns per loop
2. RIE (alternative): A single step O2 RIE process. Two 4” wafers run side-by-side on a 10” platen.
a. Gas: 50 sccm O2
RF Power: 150 W
Time: 50 minutes
b. Etch rate: approximately 0.19 microns per minute.

5.4 STRIP PHOTORESIST MASK
Note: Parylene C dies may begin to lift off from wafer during this step.
Materials: | Acetone
| Isopropanol (IPA)
Equipment: | Glass dishes designated for photoresist stripping
1. Perform chemical work in solvents fume hood
2. Soak wafer in acetone bath for 5 minutes.
3. Soak wafer in isopropanol bath for 5 minutes.
4. Soak in DI water briefly (<2 minutes)
5. Carefully blow dry if possible

## 6 RELEASE MEAS

Note: Parylene C MEAs often curl following release due to inter-layer stress.

Equipment: | Scalpel
| Microneedles
| Sharp tweezers
| Stereoscope
1. To remove a tabulated sheet:
a. Place a droplet of water at the sheet edge.
b. Looking through a stereoscope, use a scalpel or microneedle to gently lift the edge of
| the device, allowing the water to wick between the Parylene and the wafer
c. If needed, tug very gently at the edge of the sheet or along a handling tab using
| tweezers.
i. Add more water as needed

Prepared by: PIE Foundry | Reviewed by: Kee Scholten | Page 10 of 12

## 7 POST-PROCESS ANNEALING

7.1 RELEASE STRESS (FLATTEN)
Materials: | Ceramic plates
| Isopropanol
Equipment: | Hot Plate
1. Lay released MEAs flat on a ceramic plate. A few drops of isopropanol may help pull MEAs flat using surface tension.
2. Cover with second ceramic plate and place on hot plate.
3. Set hot plate to 115 °C. Wait 15 minutes after the hot plate has reached temperature and return to < 60 °C temperature. Allow plates and MEAs to cool on hot plate.

7.2 HIGH TEMPERATURE VACUUM ANNEAL
Materials: | Ceramic plates
Equipment: | Vacuum oven capable of reaching > 200 °C
1. Sandwich released MEAs between clean ceramic plates and place in vacuum oven
2. Pump down vacuum oven.
3. Anneal 275 °C with a soak time of 5 hours.

7.3 VACUUM ANNEAL
Materials: | Ceramic plates
Equipment: | Vacuum oven with N2
1. Sandwich released MEAs between clean ceramic plates and place in vacuum oven
2. Pump down vacuum oven, then rinse 3× with N2.
3. Anneal 200 °C with a soak time of 48 hours, and a ramp up/down time of 8 hours.

## 8 POST-PROCESS CLEANING

Note: this step is recommended to remove any remaining scum on electrode sites and improve impedance values
Materials: | Prime silicon wafer(s) or soda lime wafer(s)
| Kapton tape
Equipment: | Asher
1. Attach released devices to a clean carrier wafer (Si or glass) with the electrode sites exposed using small pieces of Kapton tape
2. Clean devices in the asher using the following recipe:
300 mT, 100 W, 300 S

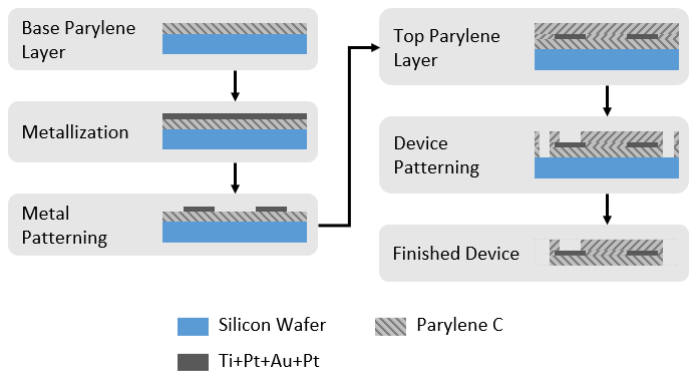
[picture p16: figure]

Prepared by: PIE Foundry | Reviewed by: Kee Scholten | Page 11 of 12
A. PROCESS FLOW DIAGRAM

Prepared by: PIE Foundry | Reviewed by: Kee Scholten | Page 12 of 12
B. MATERIAL SOURCES
Note: Standard materials (e.g. acetone, DI water, cleanroom wipes, etc.) are not listed
Material | Supplier
Parylene dimer | Specialty Coating Systems, Indianapolis, IN
AZ 12XT-20PL-15 photoresist | AZ Electronic Materials, Branchburg, NJ
AZ 5214 E photoresist | AZ Electronic Materials, Branchburg, NJ
AZ 340 developer | AZ Electronic Materials, Branchburg, NJ
AZ 726MIF developer | AZ Electronic Materials, Branchburg, NJ
Edge Bead Removal (EBR) solvent | AZ Electronic Materials, Branchburg, NJ
NMP Rinse | AZ Electronic Materials, Branchburg, NJ
Titanium | Provided by USC cleanroom
Platinum | Provided by USC cleanroom
Gold | Provided by USC cleanroom
Nanostrip 2X | CMC Materials, Santa Ana, CA
C. EQUIPMENT MODELS
Note: Standard equipment (e.g. tweezers, microscopes, N2 gun, scale, etc.) are not listed
Equipment | Model # | Supplier
Vacuum oven with N2 | TVO-2 | Cascade Tek Inc., Longmont, CO
| VO914A | Lindberg/Blue M, New Columbia, PA
Profilometer | DektakXT | Bruker, Billerica, MA
Spin coater | WS-400B-6NPP Lite | Laurell Technologies, North Wales, PA
Hot plate | PMC 730 Dataplate | Barnstead/Thermolyne, Dubuque, IA
| 1000-1 | Electronic Micro Systems, Sutton Coldfield, UK
Sonicating bath | 3510 | Branson Ultrasonics, Danbury, CT
DRIE | Plasmalab 100 | Oxford Instruments, Bristol, UK
RIE | PlasmaPro 80 | Oxford Instruments, Bristol, UK
| Series 85 | Technics, Pleasanton, CA
Asher | CV200RFS | Yield Engineering Systems, Fremont, CA
Mask aligner | Model 200 | OAI, San Jose, CA
E-beam evaporator | Mark 40 | CHA Industries, Livermore, CA
| PRO Line PVD 75 | Kurt J. Lesker, Jefferson Hills, PA
Parylene PVD | PDS 2010 Labcoter | Specialty Coating Systems, Indianapolis, IN

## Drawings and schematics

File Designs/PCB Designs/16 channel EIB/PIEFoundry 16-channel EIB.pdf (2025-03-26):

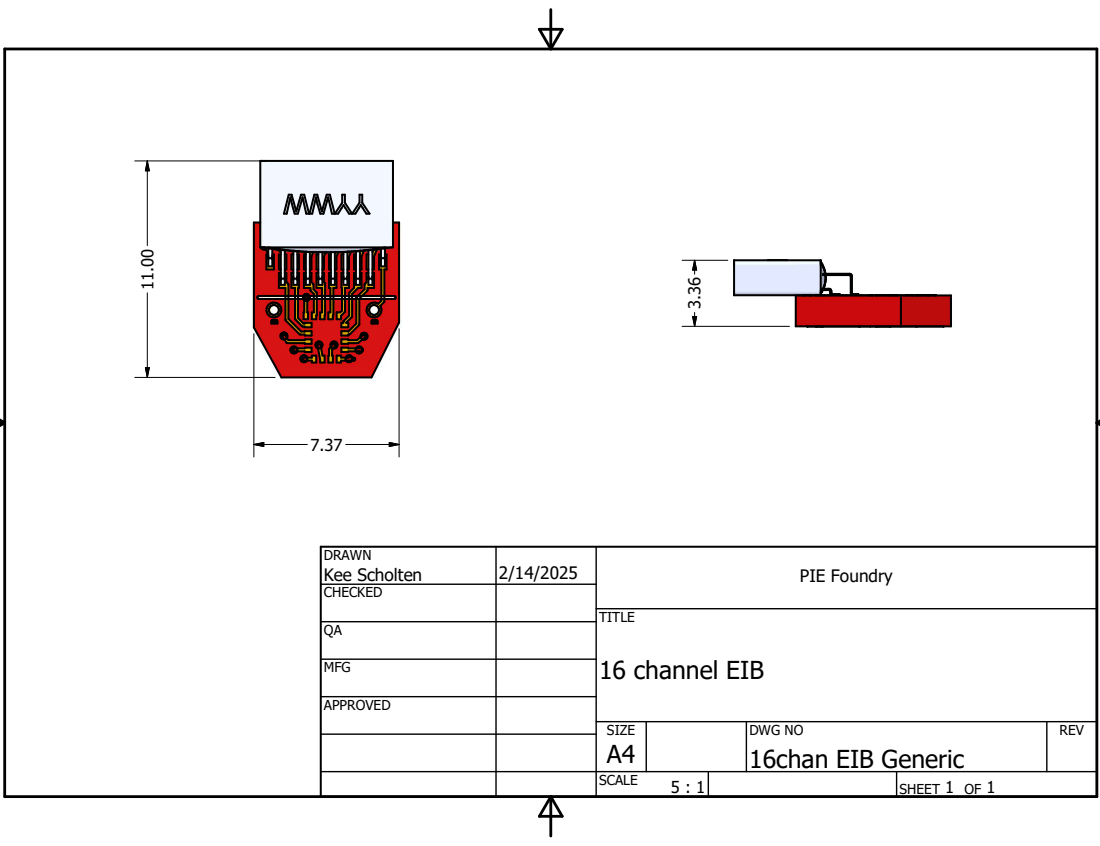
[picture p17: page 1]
TITLE; 16 channel EIB

DRAWN Kee Scholten | 2/14/2025 | PIE Foundry

CHECKED

MFG

APPROVED

SIZE A4 | DWG NO 16chan EIB Generic | REV

SCALE | | SHEET 1 OF 1

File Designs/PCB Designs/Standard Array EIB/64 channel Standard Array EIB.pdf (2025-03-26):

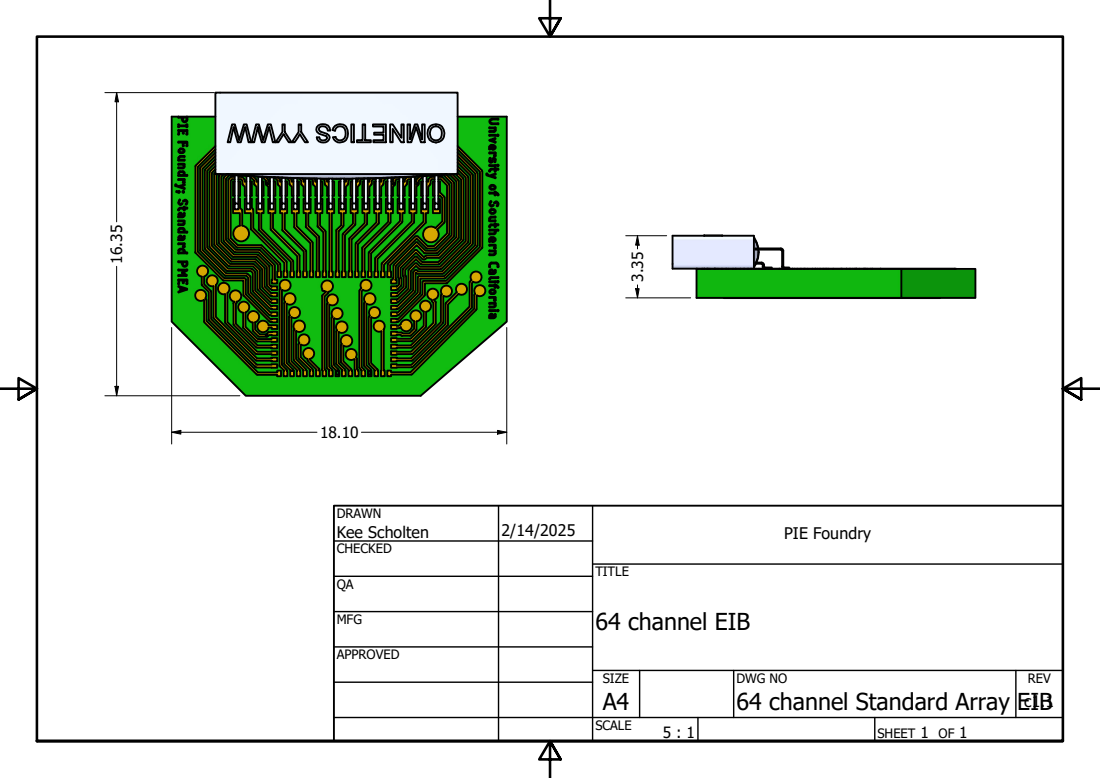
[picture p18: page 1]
64 channel EIB

DRAWN Kee Scholten | 2/14/2025 | PIE Foundry

CHECKED

MFG

APPROVED

SIZE A4 | DWG NO 64 channel Standard Array | REV EIB c1.1

SCALE 5 : 1 | | SHEET 1 OF 1

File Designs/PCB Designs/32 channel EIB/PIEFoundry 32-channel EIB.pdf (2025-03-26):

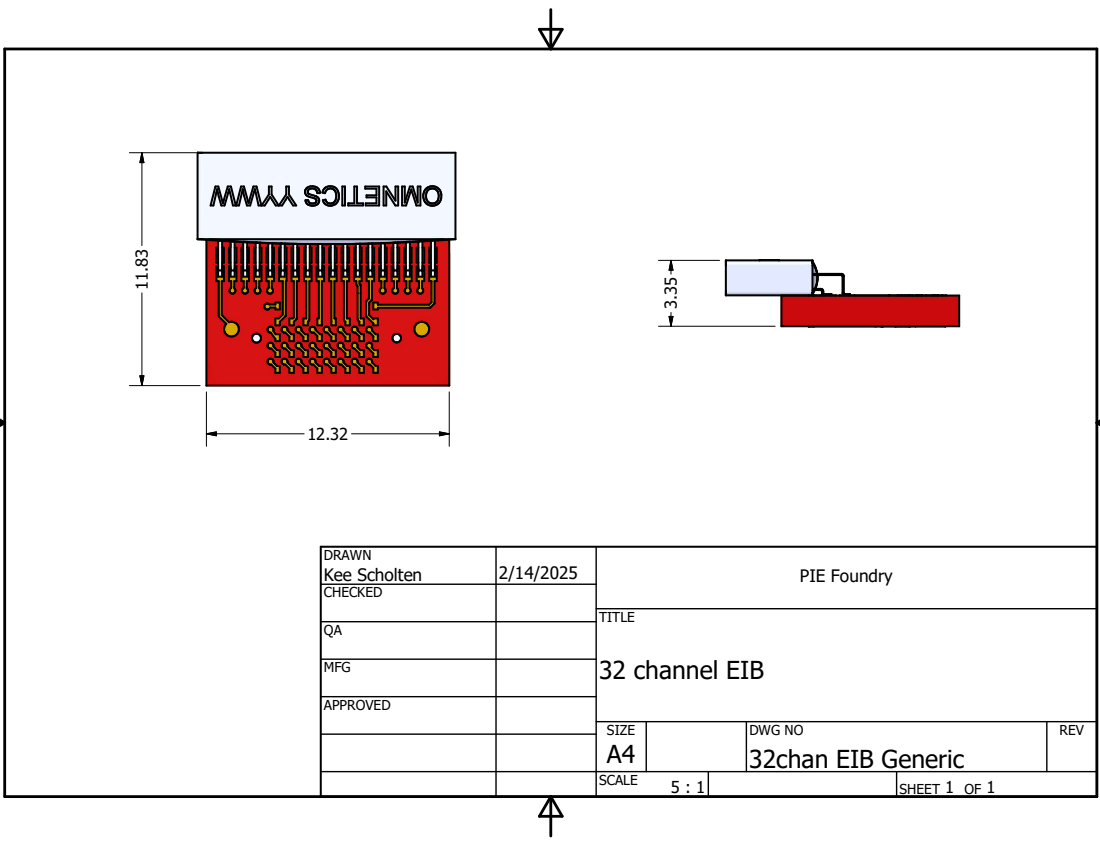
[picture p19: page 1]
TITLE; 32 channel EIB

DRAWN Kee Scholten | 2/14/2025 | PIE Foundry

CHECKED

MFG

APPROVED

SIZE A4 | DWG NO 32chan EIB Generic | REV

SCALE 5 : 1 | | SHEET 1 OF 1

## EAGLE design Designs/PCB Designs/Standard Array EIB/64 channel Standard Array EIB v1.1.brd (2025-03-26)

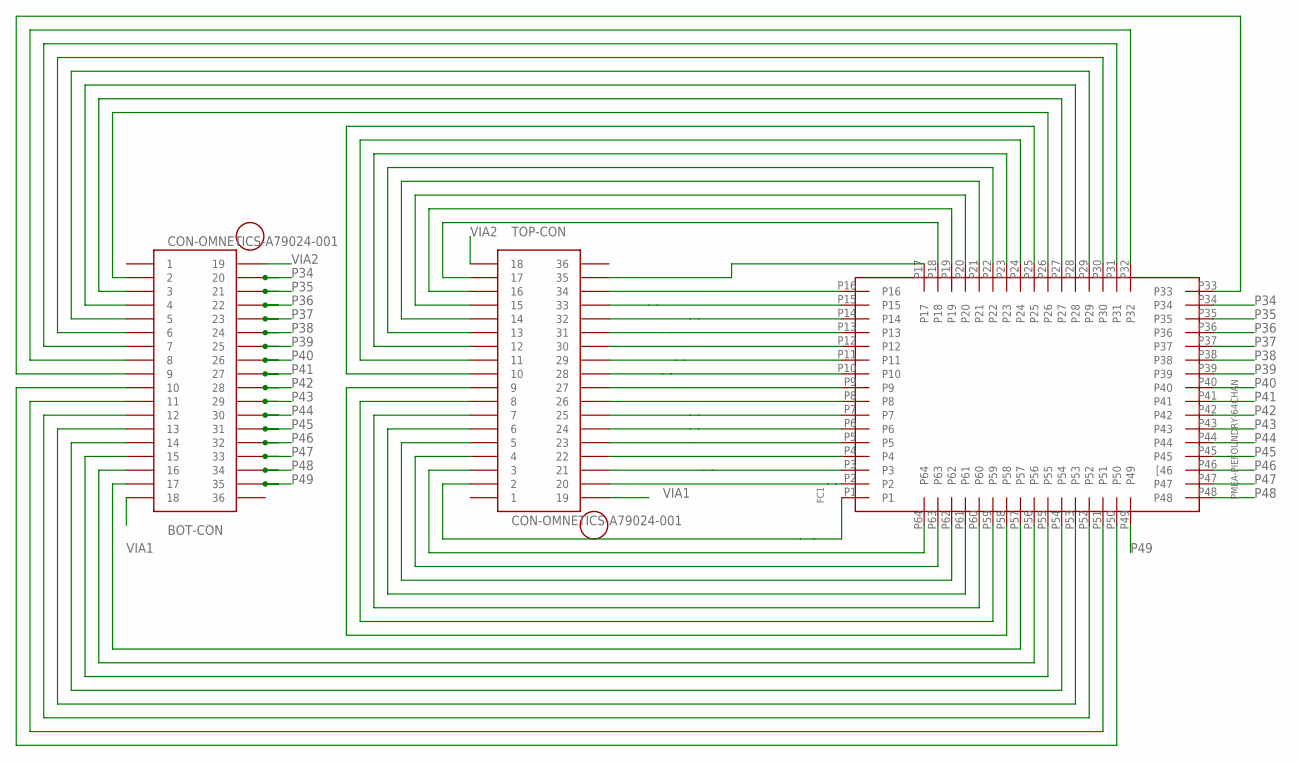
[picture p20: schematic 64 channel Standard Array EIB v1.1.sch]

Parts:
BOT-CON: CON-OMNETICS-A79024-001
FC1: PMEA-PIEFOUNDRY-64CHAN
TOP-CON: CON-OMNETICS-A79024-001

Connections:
unnamed: FC1.P17, TOP-CON.35
unnamed: FC1.P16, TOP-CON.34
unnamed: FC1.P15, TOP-CON.33
unnamed: FC1.P14, TOP-CON.32
unnamed: FC1.P13, TOP-CON.31
unnamed: FC1.P12, TOP-CON.30
unnamed: FC1.P11, TOP-CON.29
unnamed: FC1.P10, TOP-CON.28
unnamed: FC1.P9, TOP-CON.27
unnamed: FC1.P8, TOP-CON.26
unnamed: FC1.P7, TOP-CON.25
unnamed: FC1.P6, TOP-CON.24
unnamed: FC1.P5, TOP-CON.23
unnamed: FC1.P4, TOP-CON.22
unnamed: FC1.P3, TOP-CON.21
unnamed: FC1.P2, TOP-CON.20
unnamed: FC1.P18, TOP-CON.17
unnamed: FC1.P19, TOP-CON.16
unnamed: FC1.P20, TOP-CON.15
unnamed: FC1.P21, TOP-CON.14
unnamed: FC1.P22, TOP-CON.13
unnamed: FC1.P23, TOP-CON.12
unnamed: FC1.P24, TOP-CON.11
unnamed: FC1.P25, TOP-CON.10
unnamed: FC1.P1, TOP-CON.2
unnamed: FC1.P64, TOP-CON.3
unnamed: FC1.P63, TOP-CON.4
unnamed: FC1.P62, TOP-CON.5
unnamed: FC1.P61, TOP-CON.6
unnamed: FC1.P60, TOP-CON.7
unnamed: FC1.P59, TOP-CON.8
unnamed: FC1.P58, TOP-CON.9
unnamed: BOT-CON.2, FC1.P26
unnamed: BOT-CON.3, FC1.P27
unnamed: BOT-CON.4, FC1.P28
unnamed: BOT-CON.5, FC1.P29
unnamed: BOT-CON.6, FC1.P30
unnamed: BOT-CON.7, FC1.P31
unnamed: BOT-CON.8, FC1.P32
unnamed: BOT-CON.9, FC1.P33
unnamed: BOT-CON.17, FC1.P57
unnamed: BOT-CON.16, FC1.P56
unnamed: BOT-CON.15, FC1.P55
unnamed: BOT-CON.14, FC1.P54
unnamed: BOT-CON.13, FC1.P53
unnamed: BOT-CON.12, FC1.P52
unnamed: BOT-CON.11, FC1.P51
unnamed: BOT-CON.10, FC1.P50
P34: BOT-CON.20, FC1.P34
P35: BOT-CON.21, FC1.P35
P36: BOT-CON.22, FC1.P36
P37: BOT-CON.23, FC1.P37
P38: BOT-CON.24, FC1.P38
P39: BOT-CON.25, FC1.P39
P40: BOT-CON.26, FC1.P40
P41: BOT-CON.27, FC1.P41
P42: BOT-CON.28, FC1.P42
P43: BOT-CON.29, FC1.P43
P44: BOT-CON.30, FC1.P44
P45: BOT-CON.31, FC1.P45
P46: BOT-CON.32, FC1.P46 ([46)
P47: BOT-CON.33, FC1.P47
P48: BOT-CON.34, FC1.P48
P49: BOT-CON.35, FC1.P49
VIA1: BOT-CON.18, TOP-CON.19
VIA2: BOT-CON.19, TOP-CON.18

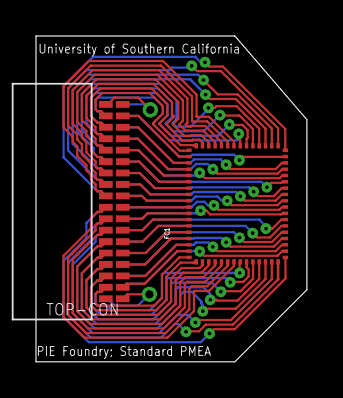
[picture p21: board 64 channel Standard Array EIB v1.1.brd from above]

Board: 2 copper layers, 15.1 x 18.1 mm, 3 parts (1 on the bottom side), 66 nets.

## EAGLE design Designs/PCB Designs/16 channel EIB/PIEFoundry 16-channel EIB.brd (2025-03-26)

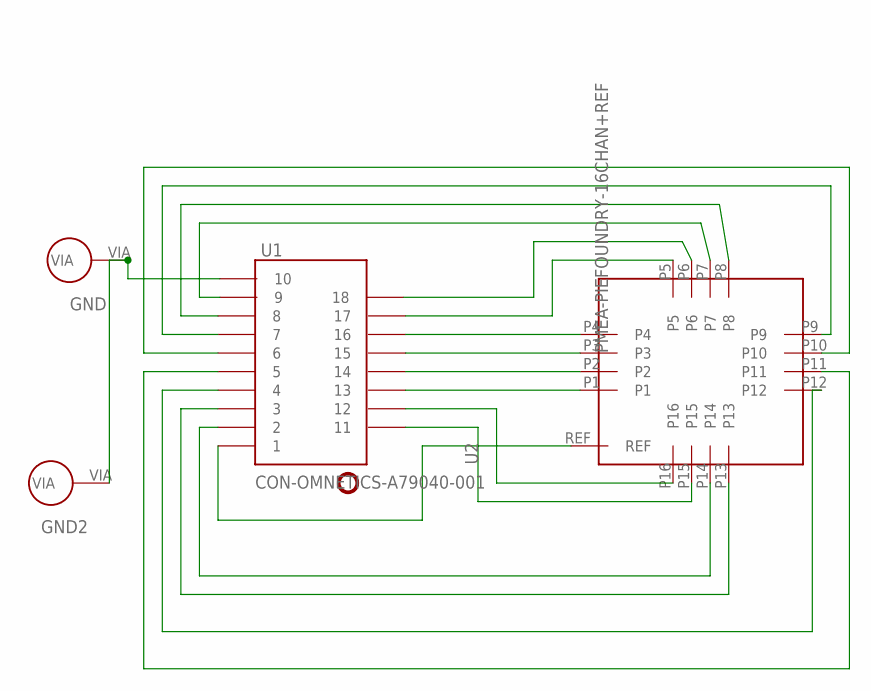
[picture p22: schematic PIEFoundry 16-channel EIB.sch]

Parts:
GND, GND2: SOLDER_VIA_500_UM
U1: CON-OMNETICS-A79040-001
U2: PMEA-PIEFOUNDRY-16CHAN+REF

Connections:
GND: GND.VIA, GND2.VIA, U1.10
unnamed: U1.13, U2.P1
unnamed: U1.14, U2.P2
unnamed: U1.15, U2.P3
unnamed: U1.16, U2.P4
unnamed: U1.12, U2.P16
unnamed: U1.11, U2.P15
unnamed: U1.17, U2.P5
unnamed: U1.18, U2.P6
unnamed: U1.2, U2.P14
unnamed: U1.3, U2.P13
unnamed: U1.8, U2.P8
unnamed: U1.9, U2.P7
unnamed: U1.4, U2.P12
unnamed: U1.5, U2.P11
unnamed: U1.6, U2.P10
unnamed: U1.7, U2.P9
unnamed: U1.1, U2.REF

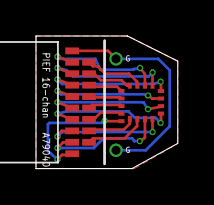
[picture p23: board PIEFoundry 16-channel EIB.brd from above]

Board: 2 copper layers, 7.9 x 7.4 mm, 4 parts (0 on the bottom side), 18 nets.

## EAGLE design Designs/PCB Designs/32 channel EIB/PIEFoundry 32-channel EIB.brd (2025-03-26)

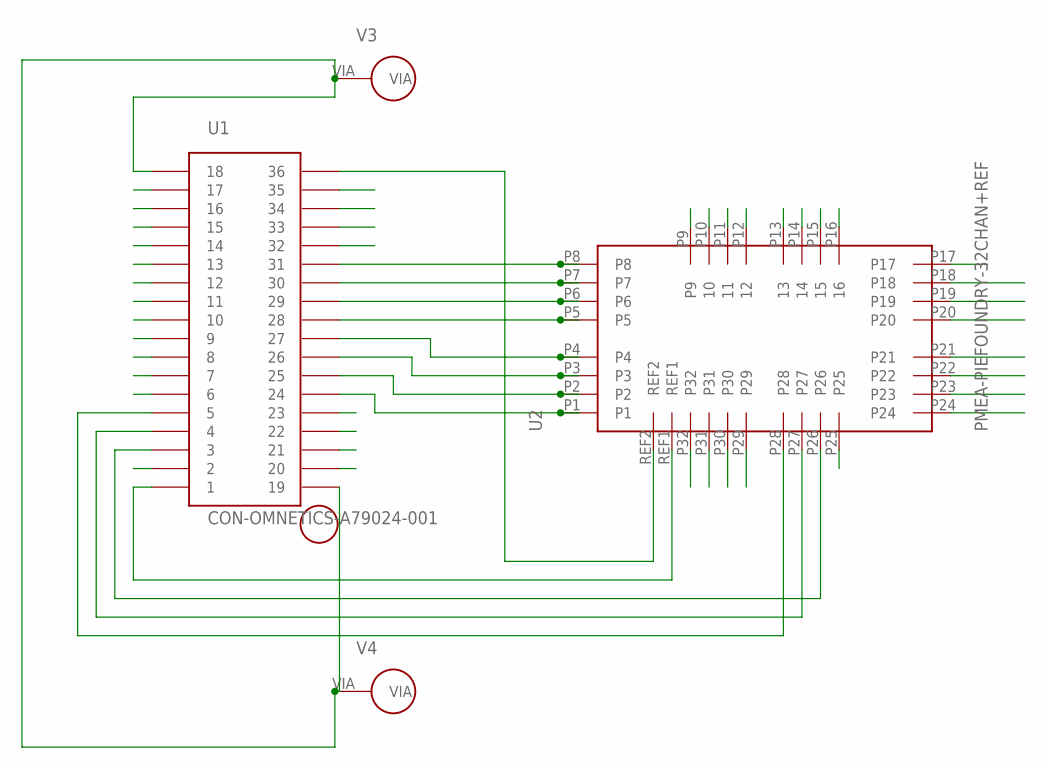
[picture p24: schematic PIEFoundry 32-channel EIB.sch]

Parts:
U1: CON-OMNETICS-A79024-001
U2: PMEA-PIEFOUNDRY-32CHAN+REF
V3, V4: SOLDER_VIA_500_UM

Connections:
GND: U1.18, U1.19, V3.VIA, V4.VIA
P1: U1.24, U2.P1
P2: U1.25, U2.P2
P3: U1.26, U2.P3
P4: U1.27, U2.P4
P5: U1.28, U2.P5
P6: U1.29, U2.P6
P7: U1.30, U2.P7
P8: U1.31, U2.P8
P9: U1.20, U2.P9
P10: U1.21, U2.P10 (10)
P11: U1.22, U2.P11 (11)
P12: U1.23, U2.P12 (12)
P13: U1.32, U2.P13 (13)
P14: U1.33, U2.P14 (14)
P15: U1.34, U2.P15 (15)
P16: U1.35, U2.P16 (16)
P17: U1.6, U2.P17
P18: U1.7, U2.P18
P19: U1.8, U2.P19
P20: U1.9, U2.P20
P21: U1.10, U2.P21
P22: U1.11, U2.P22
P23: U1.12, U2.P23
P24: U1.13, U2.P24
P25: U1.2, U2.P25
P26: U1.3, U2.P26
P27: U1.4, U2.P27
P28: U1.5, U2.P28
P29: U1.14, U2.P29
P30: U1.15, U2.P30
P31: U1.16, U2.P31
P32: U1.17, U2.P32
P33: U1.1, U2.REF1
P34: U1.36, U2.REF2

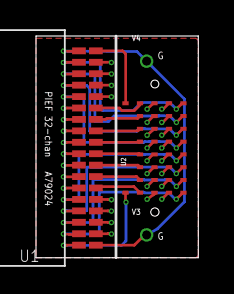
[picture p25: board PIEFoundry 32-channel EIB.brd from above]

Board: 4 copper layers, 9.0 x 12.3 mm, 4 parts (0 on the bottom side), 35 nets.

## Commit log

2024-12-30 Most recent PIE Foundry standard array CADdesigns
    [Standard Array v1.3 15micron.dxf]
2024-12-30 Rename Designs/Standard Array v1.3 15micron - MaskSet.dxf to Designs/Lithographic Designs/Standard Array v1.3 15micron - MaskSet.dxf
    Folder move
    [Standard Array v1.3 15micron - MaskSet.dxf]
2024-12-30 Rename Designs/Standard Array v1.3 15micron.dxf to Designs/Lithographic Designs/Standard Array v1.3 15micron.dxf
    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
    [Standard Array v1.3 15micron.dxf]
2024-12-30 Rename Designs/Standard Array v1.61 30 micron - MaskSet.dxf to Designs/Lithographic Designs/Standard Array v1.61 30 micron - MaskSet.dxf
    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
    [Standard Array v1.61 30 micron - MaskSet.dxf]
2024-12-30 Rename Designs/Standard Array v1.61 30 micron.dxf to Designs/Lithographic Designs/Standard Array v1.61 30 micron.dxf
    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
    [Standard Array v1.61 30 micron.dxf]
2024-12-30 Create PCB designs folder
2025-01-03 Update and rename Designs/Lithographic Designs/Standard Array v1.3 15micron - MaskSet.dxf to Designs/Lithographic Designs/Standard Array/Standard Array v1.3 15micron - MaskSet.dxf
    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
    [Standard Array v1.3 15micron - MaskSet.dxf]
2025-01-03 Update and rename Designs/Lithographic Designs/Standard Array v1.3 15micron.dxf to Designs/Lithographic Designs/Standard Array/Standard Array v1.3 15micron.dxf
    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
    [Standard Array v1.3 15micron.dxf]
2025-01-03 Update and rename Designs/Lithographic Designs/Standard Array v1.61 30 micron - MaskSet.dxf to Designs/Lithographic Designs/Standard Array/Standard Array v1.61 30 micron - MaskSet.dxf
    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
    [Standard Array v1.61 30 micron - MaskSet.dxf]
2025-01-03 Update and rename Designs/Lithographic Designs/Standard Array v1.61 30 micron.dxf to Designs/Lithographic Designs/Standard Array/Standard Array v1.61 30 micron.dxf
    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
    [Standard Array v1.61 30 micron.dxf]
2025-01-03 Rename Tetrode v1 15micron.dxf to Tetrode v1 15micron.dxf
    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
    [Tetrode v1 15micron.dxf]
2025-01-03 Tetrode v1 designs
    30 and 15 micron tetrode v1 designs
    [Tetrode v1 30micron - MaskSet.dxf, Tetrode v1 30micron.dxf]
2025-01-04 Test Structure designs
    [Test Structure v1 - MaskSet.dxf, Test Structure v1.dxf]
2025-01-04 Update and rename Designs/Lithographic Designs/Test Structure v1.dxf to Designs/Lithographic Designs/Miscellaneous/Test Structure v1.dxf
    folder move
    [Test Structure v1.dxf]
2025-01-04 Update and rename Designs/Lithographic Designs/Test Structure v1 - MaskSet.dxf to Designs/Lithographic Designs/Miscellaneous/Test Structure v1 - MaskSet.dxf
    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
    [Test Structure v1 - MaskSet.dxf]
2025-03-20 Added most recent masktemplate/alignment mark files
    [Alignment Marks v5.dxf, MaskTemplate v5.dxf]
2025-03-21 Rename Protocols/PMEA PCB Attachment.pdf to Protocols/PDFs/PMEA PCB Attachment.pdf
2025-03-22 Create PMEA PCB Attachment.md
2025-03-26 Added 16-channel EIB board file
    [PIEFoundry 16-channel EIB.brd]
2025-03-26 Created 16 channel EIB folder
    [PIEFoundry 16-channel EIB.brd]
2025-03-26 Added 16-channel EIB PCB design file set
    [PIEFoundry 16-channel EIB.dxf, PIEFoundry 16-channel EIB.sch]
2025-03-26 32-channel EIB fileset added
    [PIEFoundry 32-channel EIB.brd, PIEFoundry 32-channel EIB.dxf, PIEFoundry 32-channel EIB.sch]
2025-03-26 Rename Designs/PCB Designs/PIEFoundry 32-channel EIB.brd to Designs/PCB Designs/32 channel EIB/PIEFoundry 32-channel EIB.brd
    [PIEFoundry 32-channel EIB.brd]
2025-03-26 moved file
    [PIEFoundry 32-channel EIB.dxf]
2025-03-26 corrected folder name
    [PIEFoundry 32-channel EIB.sch]
2025-03-26 Added standard array board file
    [64 channel Standard Array EIB v1.1.brd]
2025-03-26 Updated full standard array eib fileset
    [64 channel Standard Array EIB v1.1.brd, 64 channel Standard Array EIB v1.1.dxf]
2025-03-26 Images for PCB design folder readme.md
2025-04-08 Update and rename Resources/A79016-001.stp to Resources/Solids/A79016-001.stp
    [A79016-001.stp]
2026-01-30 Revise PMEA Microfabrication protocol parameters v1.03
    Updated various parameters and processes in the PMEA Microfabrication protocol, including photoresist thickness targets, annealing temperatures, and cleaning recipes.
